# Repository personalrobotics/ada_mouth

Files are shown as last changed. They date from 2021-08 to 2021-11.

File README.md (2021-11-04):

This repo contains all of the necessary resources for using the **ADA Mouth**. 

See the mouth in action [here](https://www.youtube.com/watch?v=ZxVxqeChxVc) and [here](https://www.youtube.com/watch?v=1Y0yb5UmyZ8).

Check out the wiki for build instructions: [https://github.com/personalrobotics/ada_mouth/wiki/ADA-Mouth-Build-Guide](https://github.com/personalrobotics/ada_mouth/wiki/ADA-Mouth-Build-Guide)



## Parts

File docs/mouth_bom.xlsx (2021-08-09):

Item | Quantity | Cost per unit | Link | Notes
Typodont | 1 | $79.99 | https://plutusdental.com/collections/dental-anatomic-models/products/dental-typodont-model-860-with-columbia-removable-teeth https://www.amazon.com/Dental-Typodont-200-Kilgore-Removable/dp/B01M6DVEU7
Mounting Pole | 1 | $89.99 | https://plutusdental.com/collections/dental-anatomic-models/products/dental-typodont-mounting-pole-for-dentoform-anatomy-models https://www.amazon.com/Dental-Typodont-200-Kilgore-Removable/dp/B01M6DVEU7
Mouth Cover | 2 | $90.00 | https://plutusdental.com/collections/dental-anatomic-models/products/dental-anatomical-oral-cavity-gum-cover-for-dental-models https://www.amazon.com/Dental-Anatomy-Cavity-Cover-Models/dp/B07N8MQYF9 | Only need to buy one if you don't plan to sensorize the mouth
Servo Motor | 1 | $16.66 | https://www.amazon.com/gp/product/B01MU7TQV8
Arduino Uno | 1 | $21.98 | https://www.amazon.com/Arduino-A000066-ARDUINO-UNO-R3/dp/B008GRTSV6
Arduino Uno Cable | 1 | $6.27 | https://www.amazon.com/AmazonBasics-USB-2-0-Cable-Male/dp/B00NH11KIK/ | Any USB cable with one A-Male end and one B-Male end is fine.
Velcro | 1 | $6.97 | https://www.amazon.com/VELCRO-Brand-Fasteners-Classroom-90975W/dp/B08P3MXLLD | Any standard velcro is fine.
Power Adapter | 1 | $19.86 | https://www.amazon.com/gp/product/B07MXXXBV8
Zip Ties | 1 | $4.99 | https://www.amazon.com/gp/product/B01018DB2E
Foam Brush | 1 | $11.49 | https://www.amazon.com/gp/product/B01N10GW52
Strain Gauge | 4 | $8.20 | https://www.robotshop.com/en/elecrow-strain-gauge-module.html
Female to wire lead barrell connector | 1 | $5.04 | https://www.digikey.com/en/products/detail/tensility-international-corp/10-02247/6412282
Spool of Thin Stranded Wire | 1 | $4.25 | https://www.digikey.com/en/products/detail/pololu-corporation/2600/10451067 | Any 28 or 30 gauge stranded wire is fine.
Heat Shrink (Small) | 1 | $2.16 / 2 ft | https://www.digikey.com/en/products/detail/3m/FP301-1-16-48-BLACK-250-PCS/3864747 | Any heatshrink for 28 or 30 gauge wire is fine.
Heat Shrink (Medium) | 1 | $1.90 / 4ft | https://www.digikey.com/en/products/detail/alpha-wire/F221B1-8-BK100/281671 | Any approximately 1/8 diameter (supplied) heat shrink is fine.
Male-to-Male Jumper Cables | 1 | $1.95 | https://www.digikey.com/en/products/detail/sparkfun-electronics/PRT-12795/5993860
Female-to-Male Jumper Cables | 3 | $1.95 | https://www.digikey.com/en/products/detail/sparkfun-electronics/PRT-12794/5993859 | You only NEED to buy one, but you should buy 3 if you want everything to be nicely color coded.
Dowel Pin | 1 | $8.49 / pack of 100 | https://www.mcmaster.com/91595A558/
10mm M3 Screws | 1 | $5.92 / pack of 100 | https://www.mcmaster.com/92000A120/
M3 Hex Nuts | 1 | $2.67 / pack of 100 | https://www.mcmaster.com/90591A250/
10 mm M2 Screws | 1 | $7.67 / pack of 100 | https://www.mcmaster.com/92000A017/
14 mm M2 Screws | 1 | $7.85 / pack of 100 | https://www.mcmaster.com/92000A020/
M2 Hex Nuts | 1 | $2.06 / pack of 100 | https://www.mcmaster.com/90592A075/
M2 Screw Inserts | 1 | $14.98 / pack of 25 | https://www.mcmaster.com/94510A360/
20 mm M5 Screws | 1 | $16.53 / pack of 50 | https://www.mcmaster.com/90751A124/
M5 Hex Nuts | 1 | $1.76 / pack of 100 | https://www.mcmaster.com/90592A095/
Plastic Bag | 1 | $1.92 /pack of 100 | https://www.mcmaster.com/1959T11/ | The strain gauges came with small bags that I used instead of buying these. But if yours don't come with bags, you can buy this.
Additional Tools
3D Printer
Soldering Iron
Heat Gun (or any other method for activating heat shrink)
Tweezers
Wire Cutter/Stripper
Phillips/Flat Head Screw Driver
Allen Keys for M5 Screw
Scissors
Exacto Knife
Sharpie/Marker
Hot Glue Gun (Optional)

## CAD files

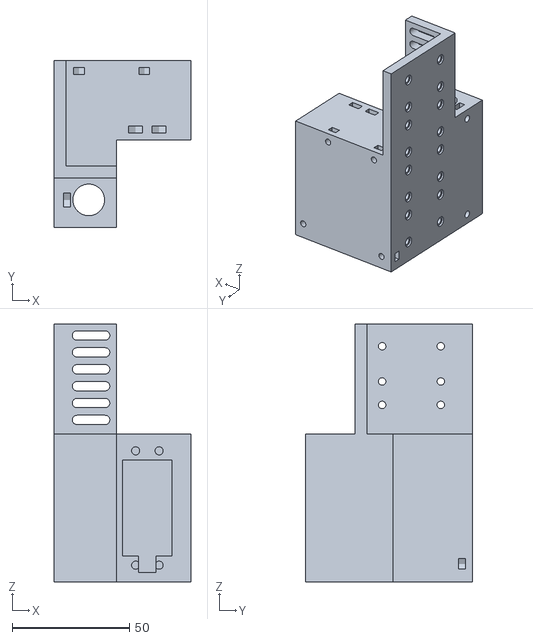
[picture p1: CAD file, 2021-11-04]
mouth_hw/STL/mouth_circuitry_mount.stl
58.3 x 71.2 x 110.0

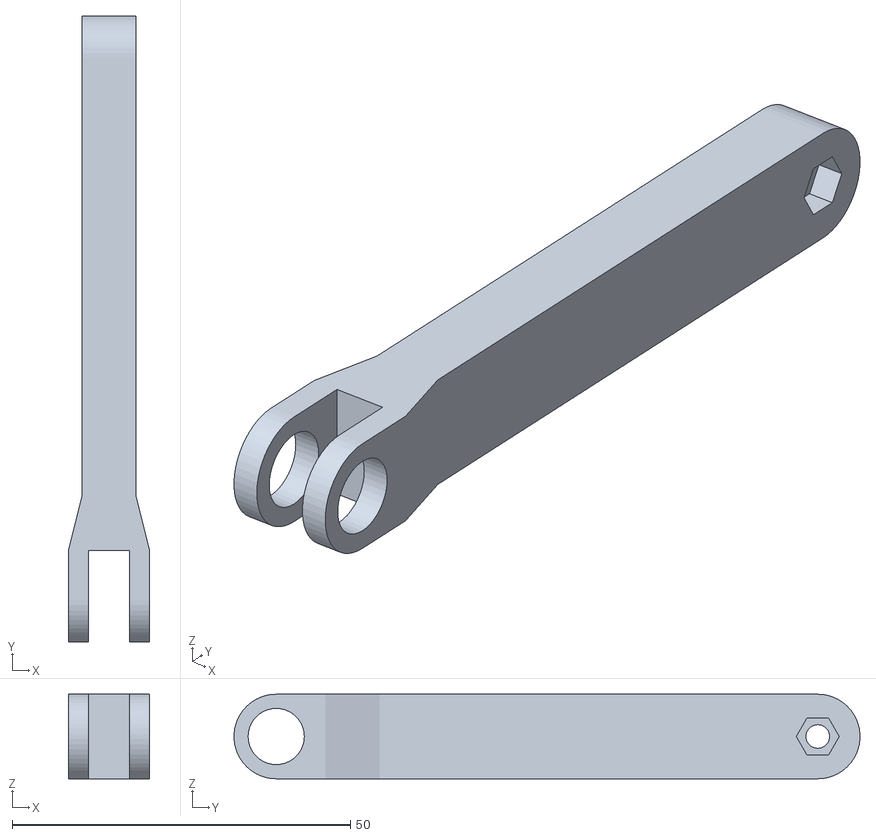
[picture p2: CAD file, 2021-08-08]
mouth_hw/STL/mouth_servo_link.stl
12.0 x 92.5 x 12.5

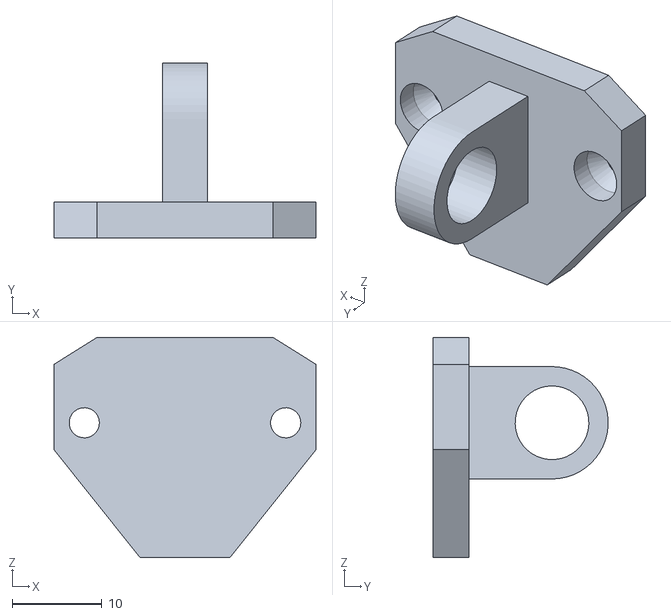
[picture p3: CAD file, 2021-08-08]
mouth_hw/STL/mouth_joint.stl
29.1 x 19.5 x 24.5

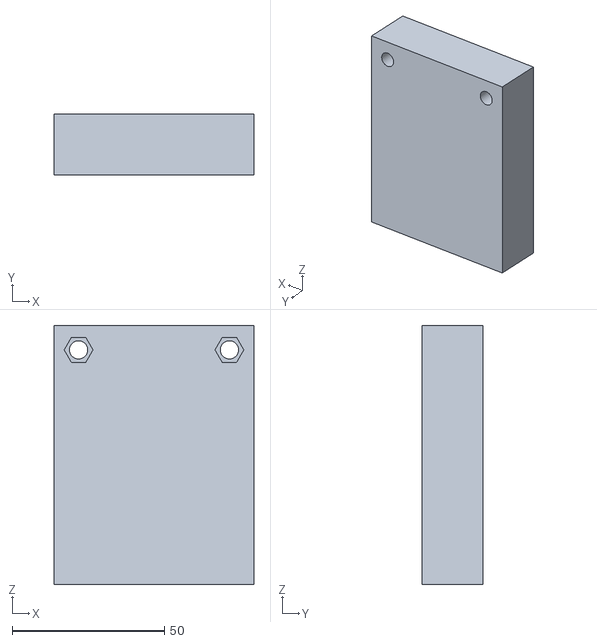
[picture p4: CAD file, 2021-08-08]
mouth_hw/STL/mouth_base_mount.stl
65.6 x 20.0 x 85.0

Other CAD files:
mouth_hw/CAD/mouth_base_mount.f3d
mouth_hw/CAD/mouth_parts.f3d

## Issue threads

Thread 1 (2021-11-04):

### ISSUE TITLE
Circuitry Mount Assembly: Where to insert the screw inserts is unclear

### ISSUE THREAD

**Issue by TrueshotBarrage** [personalrobotics/ada_mouth#1]
**Summary: Steps 5-8 for the circuitry mount assembly documentation are unclear and are consequently hard to follow when building the mouth model.**

> Step 5: Use a soldering iron to gently push an M2 screw insert into **each of the 16 holes** on the back of the circuitry mount.

First, the orientation of the circuitry mount should be specified. "Front" or "back" do not make sense without a reference frame. Regardless, there doesn't seem to be any set of 16 holes on any of the surfaces in the 3d STL file. As such, it is impossible to follow the rest of the instructions in the section, as the location of the strain gauges is unclear.

**Comment by TrueshotBarrage** [comment]
![Strain gauge board](https://github.com/personalrobotics/ada_mouth/wiki/images/resolder_stain_gauge.png)

Judging from this image, there seems to be a different/additional part that is not included in the documentation. The [mouth_circuitry_mount.stl](https://github.com/personalrobotics/ada_mouth/blob/master/mouth_hw/STL/mouth_circuitry_mount.stl) only includes the lower half of what is displayed in the image.

**Comment by palanc** [comment]
Thanks for pointing this out, we had accidentally posted an older version of that part. It is updated now.

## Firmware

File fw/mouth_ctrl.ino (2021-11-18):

#include <Servo.h>

#define MAX_SERVO_CMD 90 // The max value servo cmd accepted
#define MIN_SERVO_CMD 20 // The min value servo cmd accepted

#define SERIAL_BAUD_RATE 9600 // Serial communication speed
#define SERVO_PIN 9 // Pin number of output to servo

#define TRANSFER_RATE 20 // Rate at which to output strain gauge data
#define SENSOR_COUNT 4  // Number of strain gauge sensors
#define LEFT_SENSOR_PIN A0 // Pin for sensor on left side of mouth
#define RIGHT_SENSOR_PIN A1 // Pin for sensor on right side of mouth
#define TOP_SENSOR_PIN A2 // Pin for sensor on roof of mouth
#define BOTTOM_SENSOR_PIN A3 // Pin for sensor on floor of mouth

Servo servo;
unsigned long last_sample = 0; // Timestamp of previous sensor sample sent
uint8_t sensor_buff[2*SENSOR_COUNT]; // Write buffer for sensor data
unsigned int led_count = 0;

// Initialize the mouth
void setup() {
  Serial.begin(SERIAL_BAUD_RATE);
  servo.attach(SERVO_PIN);

  delay(10);

  // Open the mouth by default
  servo.write(MIN_SERVO_CMD);
  
  pinMode(LED_BUILTIN, OUTPUT);
  digitalWrite(LED_BUILTIN, HIGH);
}

void loop() {

  // Process servo commands
  if(Serial.available() > 0) { // Check if cmd has come in
    int servo_cmd = Serial.read(); // Read the cmd
    
    // Check if cmd is in range
    if(servo_cmd >= MIN_SERVO_CMD && servo_cmd <= MAX_SERVO_CMD) {
      servo.write(servo_cmd); // Send cmd to servo
    }
  }
  
  // Read sensor vals from strain gauge boards
  int left_sensor_val = analogRead(LEFT_SENSOR_PIN);
  int right_sensor_val = analogRead(RIGHT_SENSOR_PIN);
  int top_sensor_val = analogRead(TOP_SENSOR_PIN);
  int bottom_sensor_val = analogRead(BOTTOM_SENSOR_PIN);

  unsigned long now = millis();
  float elapsed = (now - last_sample) / 1000.0;
  // Check if it is time to send data
  if(elapsed > 1.0/TRANSFER_RATE) {
    last_sample = now;

    // Each strain gauge reading is serialized 
    // into two bytes, where the 5 lsb of each
    // byte contain the data
    sensor_buff[0] = left_sensor_val & 0x01F;
    sensor_buff[1] = left_sensor_val >> 5;
    sensor_buff[2] = right_sensor_val & 0x01F;
    sensor_buff[3] = right_sensor_val >> 5;
    sensor_buff[4] = top_sensor_val & 0x01F;
    sensor_buff[5] = top_sensor_val >> 5;
    sensor_buff[6] = bottom_sensor_val & 0x01F;
    sensor_buff[7] = bottom_sensor_val >> 5;   

    // Add an id to the 3 msb of each byte
    for(int i = 0; i < 2*SENSOR_COUNT; i++) {
      sensor_buff[i] |= (i << 5); 
    }

    // Send the data to host         
    Serial.write(sensor_buff, 2*SENSOR_COUNT);

    if(led_count < TRANSFER_RATE/2)
    {
      digitalWrite(LED_BUILTIN, HIGH);
    } else {
      digitalWrite(LED_BUILTIN, LOW);
    }
    led_count = (led_count + 1) % TRANSFER_RATE;
  }
  
}

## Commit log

2021-08-08 Added bill of materials
    [mouth_bom.xlsx]
2021-08-08 Added cad design files
    [mouth_arduino_mount.stl, mouth_base_mount.f3d, mouth_base_mount.stl, mouth_joint.stl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]
2021-08-08 Updated BOM
    [mouth_bom.xlsx]
2021-08-08 Renamed stl file
    [mouth_circuitry_mount.stl]
2021-08-09 Update bom
    [mouth_bom.xlsx]
2021-08-09 Updated bom, changed stl name
    [mouth_bom.xlsx, mouth_servo_link.stl]
2021-08-09 Added firmware for Arduino Uno
2021-11-04 Fix circuitry mount stl
    [mouth_circuitry_mount.stl]
2021-11-18 Modified arduino fw to blink an led
